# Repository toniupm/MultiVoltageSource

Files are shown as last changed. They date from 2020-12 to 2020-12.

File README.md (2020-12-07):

# MultiVoltageSource

<b> Design and Programming by Antonio Perez-Serrano </b> 

<b> PCB Design by Jose David Ayala </b> 

<i> CEMDATIC - ETSI Telecomunicación, Universidad Politécnica de Madrid (UPM) </i>

Version 1.0 - December 2020

<p align="center">
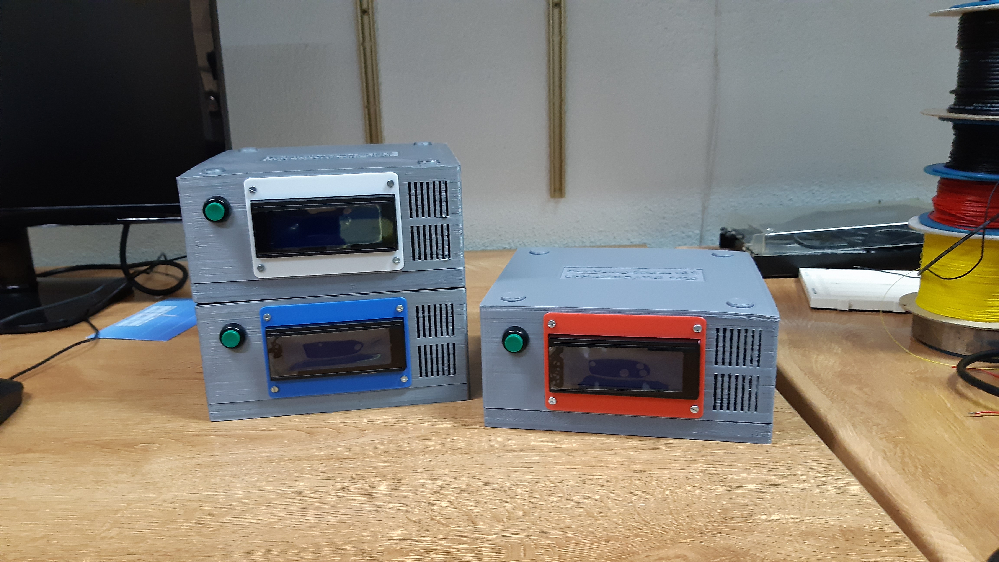
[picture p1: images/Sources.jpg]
MultiVoltageSources finished and ready to work.

</p>

<p align="justify"> Here we describe the MultiVoltageSource project, a voltage source with 7 channels used to power up photonic integrated circuits. </p>

<p align="justify">
     The <b> hardware </b> is based on negative linear regulators <a href="https://www.analog.com/en/products/lt3090.html#product-overview" target="_blank">LT3090</a> and digital potentiometers <a href="https://www.analog.com/en/products/ad5290.html" target="_blank">AD5290</a> controlled by an Arduino Nano <a href="https://store.arduino.cc/arduino-nano-every" target="_blank">Every</a> or <a href="https://store.arduino.cc/arduino-nano-33-iot" target="_blank">33 IOT</a>. It offers 7 channels ranging from -0.2 V to -10.2 V. A power supply of &plusmn; 15 V or &plusmn; 12 V is needed. The current output of the power supply must be choosen depending on the application, in our case a current output of 0.5 A is enough. The schematics and PCB design have been created using <a href="https://kicad.org/" target="_blank">KiCad</a> and they can be found in the <i> Kicad Project </i> folder. The MultiVoltageSource box has been designed using <a href="https://www.blender.org/" target="_blank">Blender</a>, it can be found in the <i> Blender Project </i> folder. The box can be 3D printed using PLA or ABS material and it is designed to use M3 bolts and nuts. The MultiVoltageSource is controlled via serial port, this allows to program voltage sweeps easily.   
</p>

<p align="center">
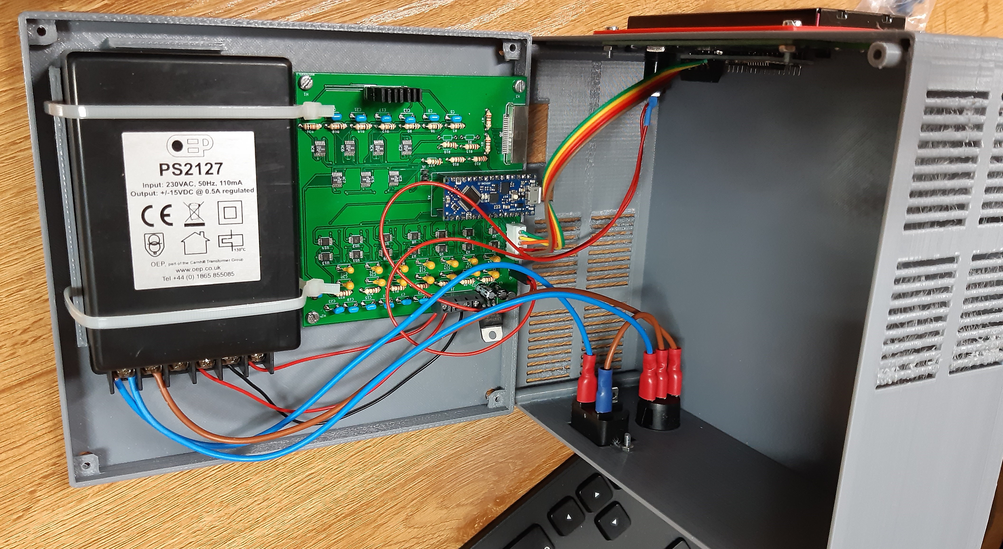
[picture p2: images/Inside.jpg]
Inside a MultiVoltageSource.

</p>

<p align="justify">
     The list of the materials used are:
     <ul>
          <li> 1 Arduino Nano <a href="https://store.arduino.cc/arduino-nano-every" target="_blank">Every</a> or <a href="https://store.arduino.cc/arduino-nano-33-iot" target="_blank">33 IOT</a> </li>
          <li> 7 chips <a href="https://www.analog.com/en/products/lt3090.html#product-overview" target="_blank">LT3090</a> </li>
          <li> 14 chips <a href="https://www.analog.com/en/products/ad5290.html" target="_blank">AD5290</a> </li>
          <li> 1 LCD display 20x4 characters </li>
          <li> 1 i2c/SPI LCD backpack <a href="https://learn.adafruit.com/i2c-spi-lcd-backpack" target="_blank">i2c/SPI LCD backpack</a> with the SPI enabled </li>
          <li> 1 Embedded Linear Power Supply Encapsulated PS2127 &plusmn; 15 V</li>
          <li> 1 Voltage Regulator to 5 V LD1085V50 </li>
          <li> 7 Resistors 2k &#8486; </li>
          <li> 7 Resistors 2.2k &#8486; </li>
          <li> 7 Resistors 10k &#8486; </li>
          <li> 7 Capacitors 4.7 uF </li>
          <li> 2 Capacitors 10 uF </li>
          <li> 14 Capacitors 100 nF </li>
          <li> Several PCB connectors including 1 <a href="https://www.samtec.com/products/fcs8-20-01-l-s-a-tr" target="_blank">FCS8-20-01-L-S-A-TR</a> connector </li>
          <li> 1 Switch </li>
          <li> 1 Button </li>
          <li> 1 Power Supply cable and connector </li>
          <li> Several cables </li>
     </ul>          
</p>

The cost of a MultiVoltage source is around 200 €.

<p align="center">
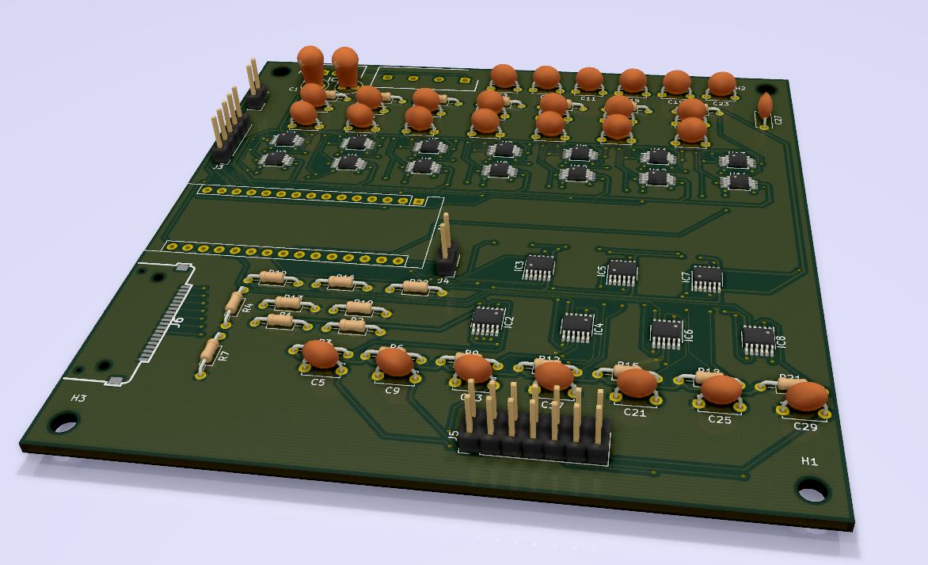
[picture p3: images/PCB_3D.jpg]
KiCad rendering of the PCB.

</p>

<p align="justify">
     The <b> software </b> can be found in the <i> Software </i> folder. It contains the Arduino Firmware and the LabVIEW project and functions to control the MultiVoltageSource. LabVIEW 2020 version has been used to create the controlling software. At this moment, only serial communication through a USB cable is supported. Next versions will include WiFi communication.   
</p>

<p align="center">
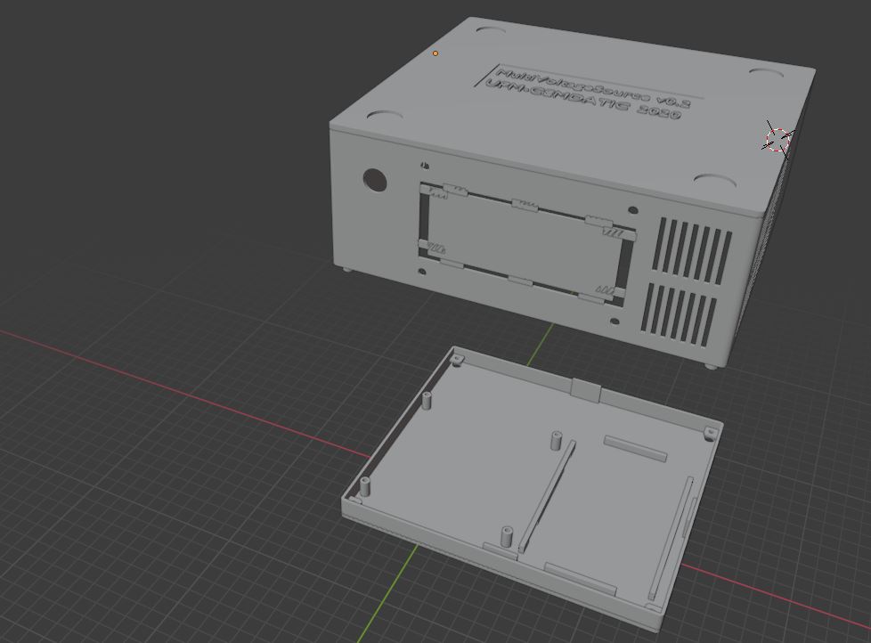
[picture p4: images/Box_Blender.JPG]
Blender snapshot of the box.

</p>

<p align="justify">
     Future improvements/changes:
          <ul>
               <li> WiFi communication using Arduino Nano 33 IOT </li>
               <li> Creation a stand-alone control software based on Processing </li>
          </ul>     
</p>

<p align="center">
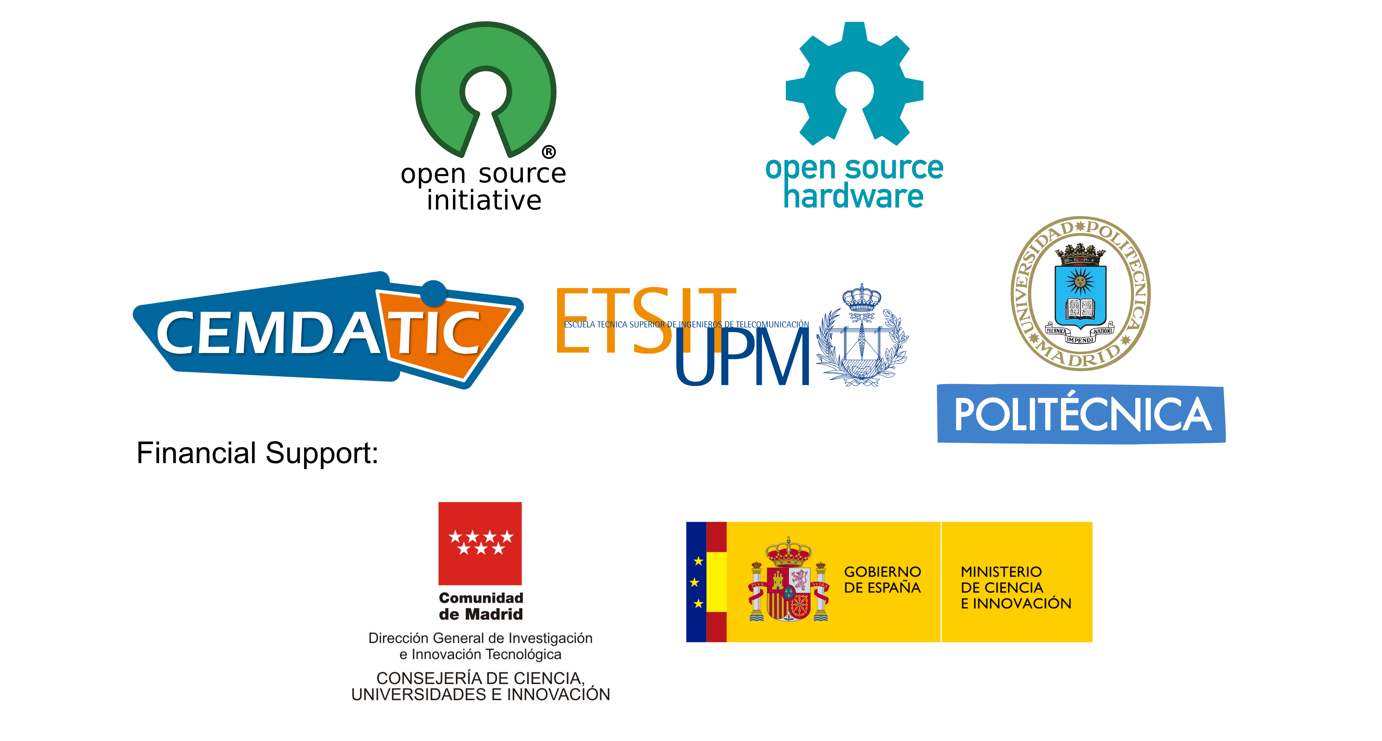
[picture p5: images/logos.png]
Logos

</p>

<p align="justify">
We acknowledge support from Comunidad de Madrid through project MULTI-GAS-PIC (APOYO-JOVENES-KXHJ8C-16-VCKM78) and Ministerio de Ciencia e Innovación of Spain through project LIDERA (RTI2018-094118-B-C21).
</p>

<p align="justify">
"Acción financiada por la Comunidad de Madrid en el marco del Convenio Plurianual con la Universidad Politécnica de Madrid <b> en la línea de actuación estímulo a la investigación de jóvenes doctores </b>"
</p>

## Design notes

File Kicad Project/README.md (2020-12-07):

This folder contains the KiCad project of the MultiVoltageSource, including schematics, PCB and final Gerber files.

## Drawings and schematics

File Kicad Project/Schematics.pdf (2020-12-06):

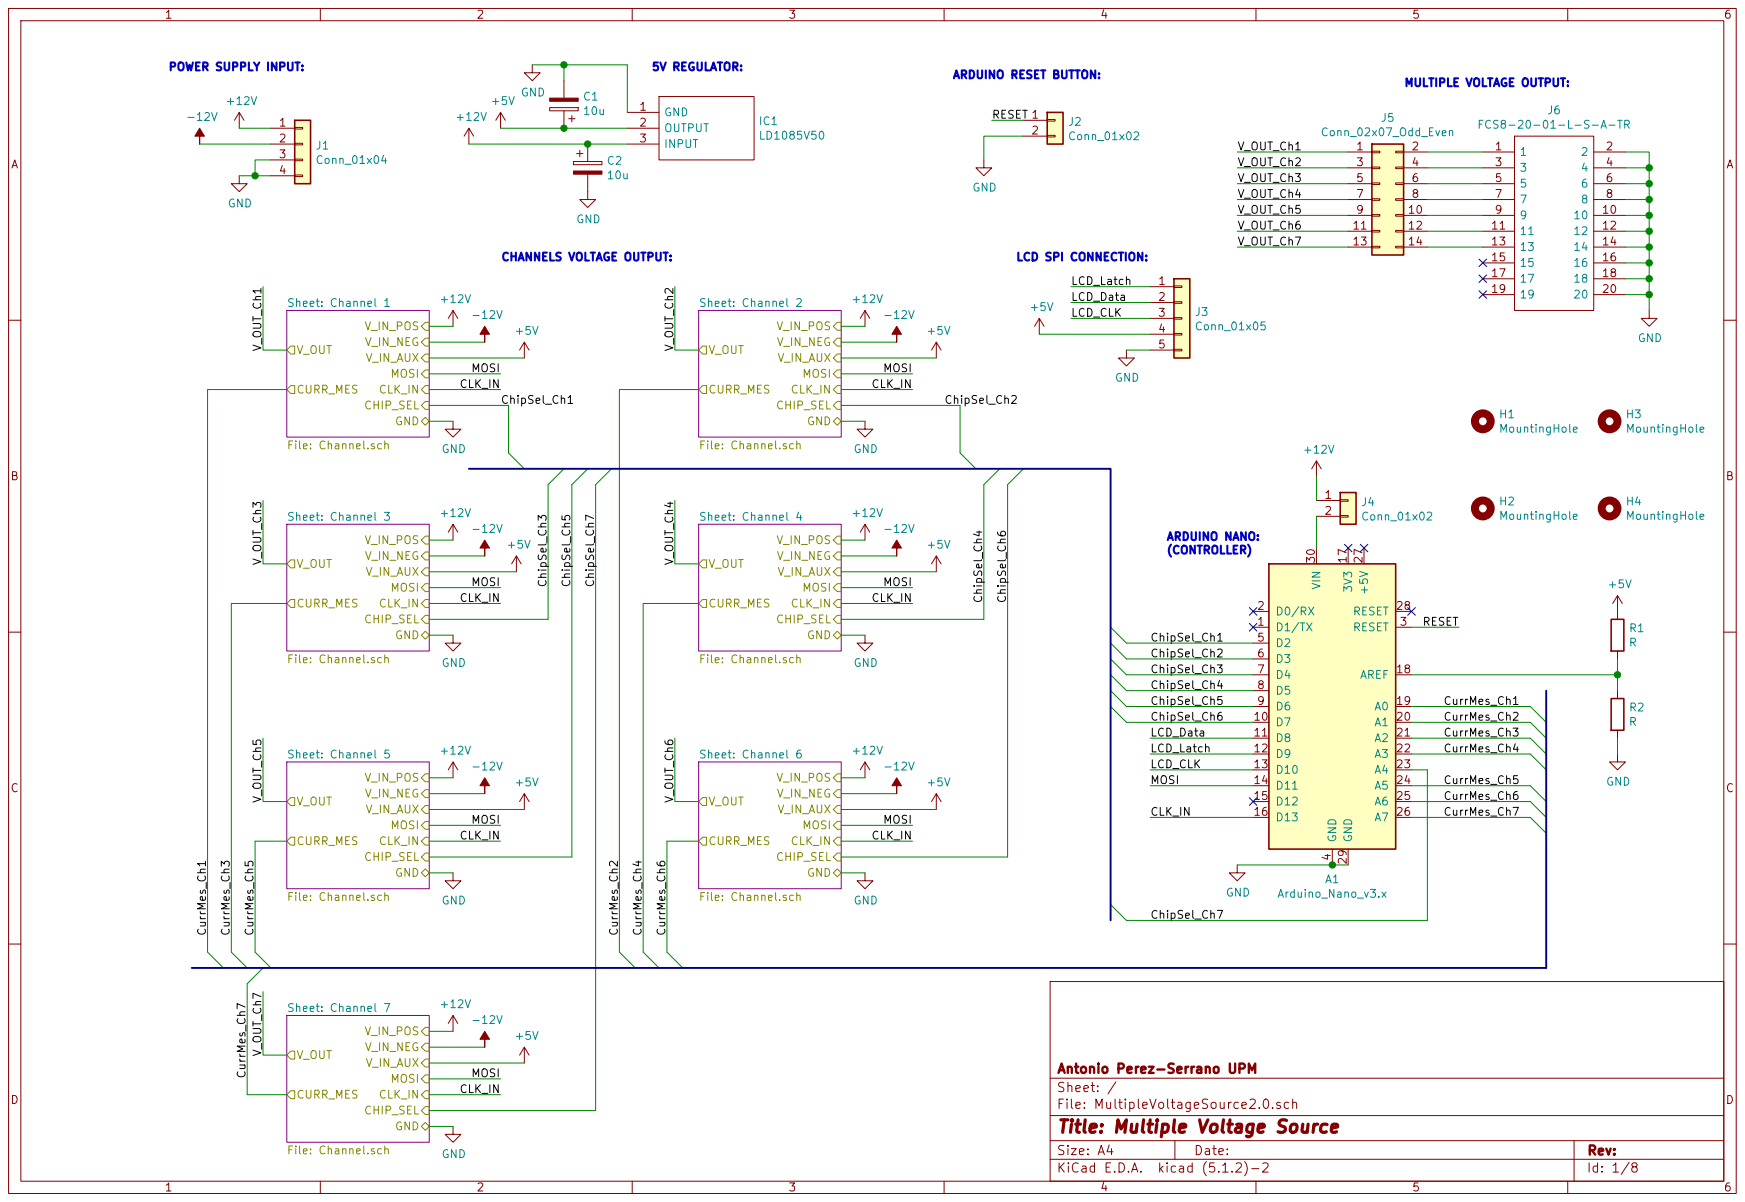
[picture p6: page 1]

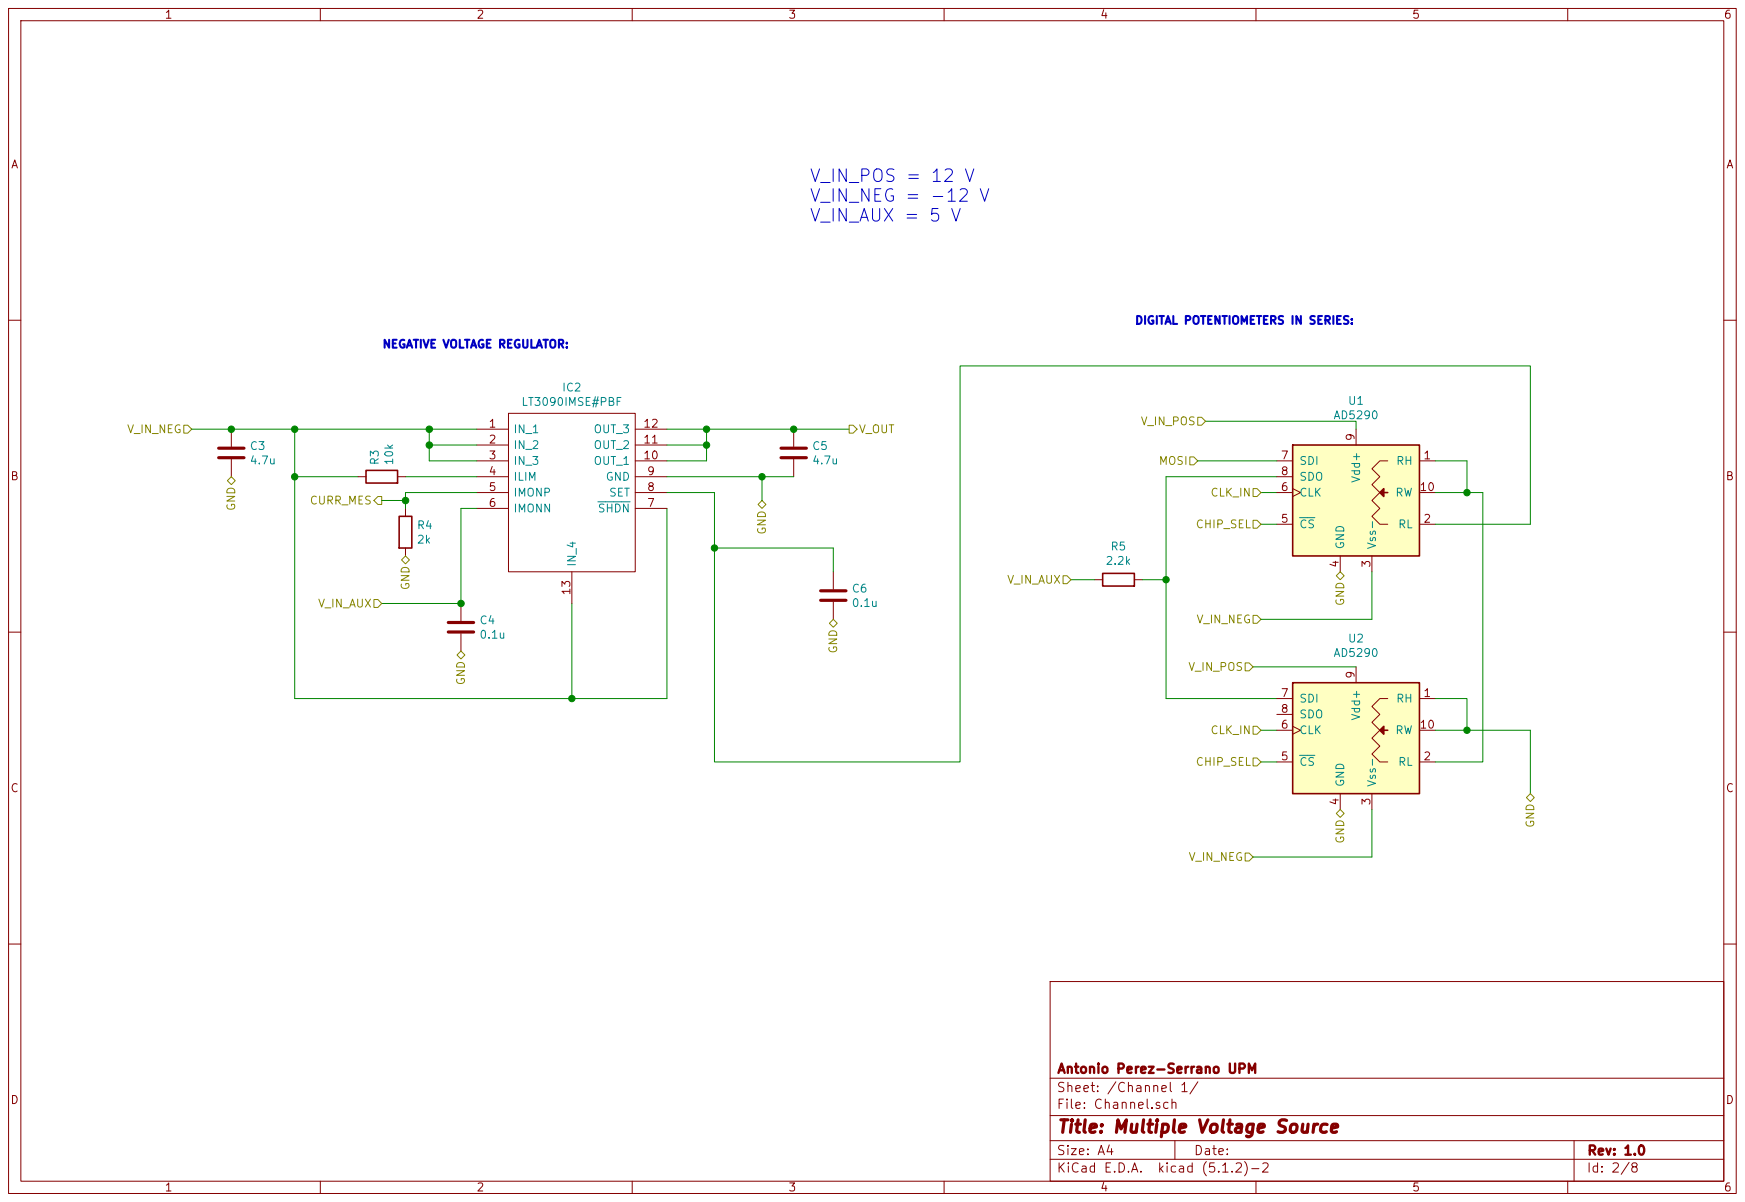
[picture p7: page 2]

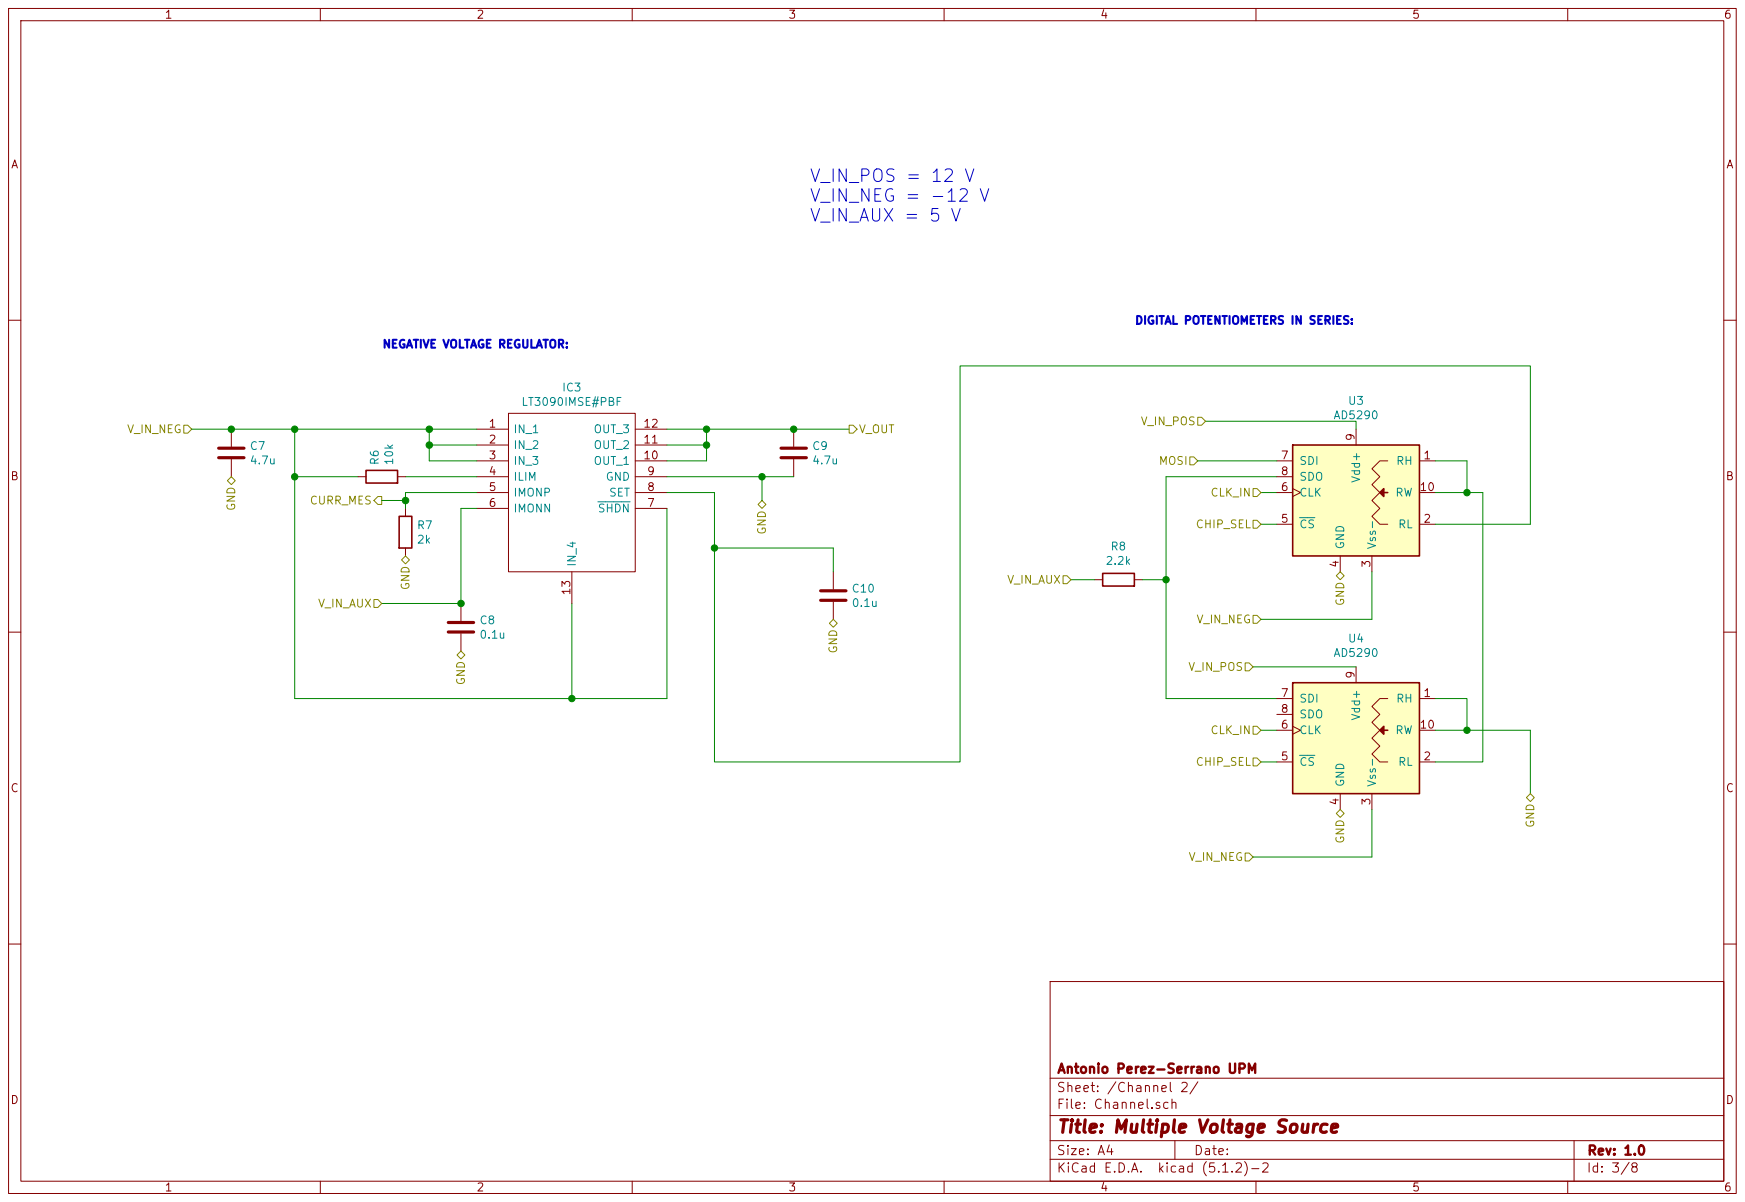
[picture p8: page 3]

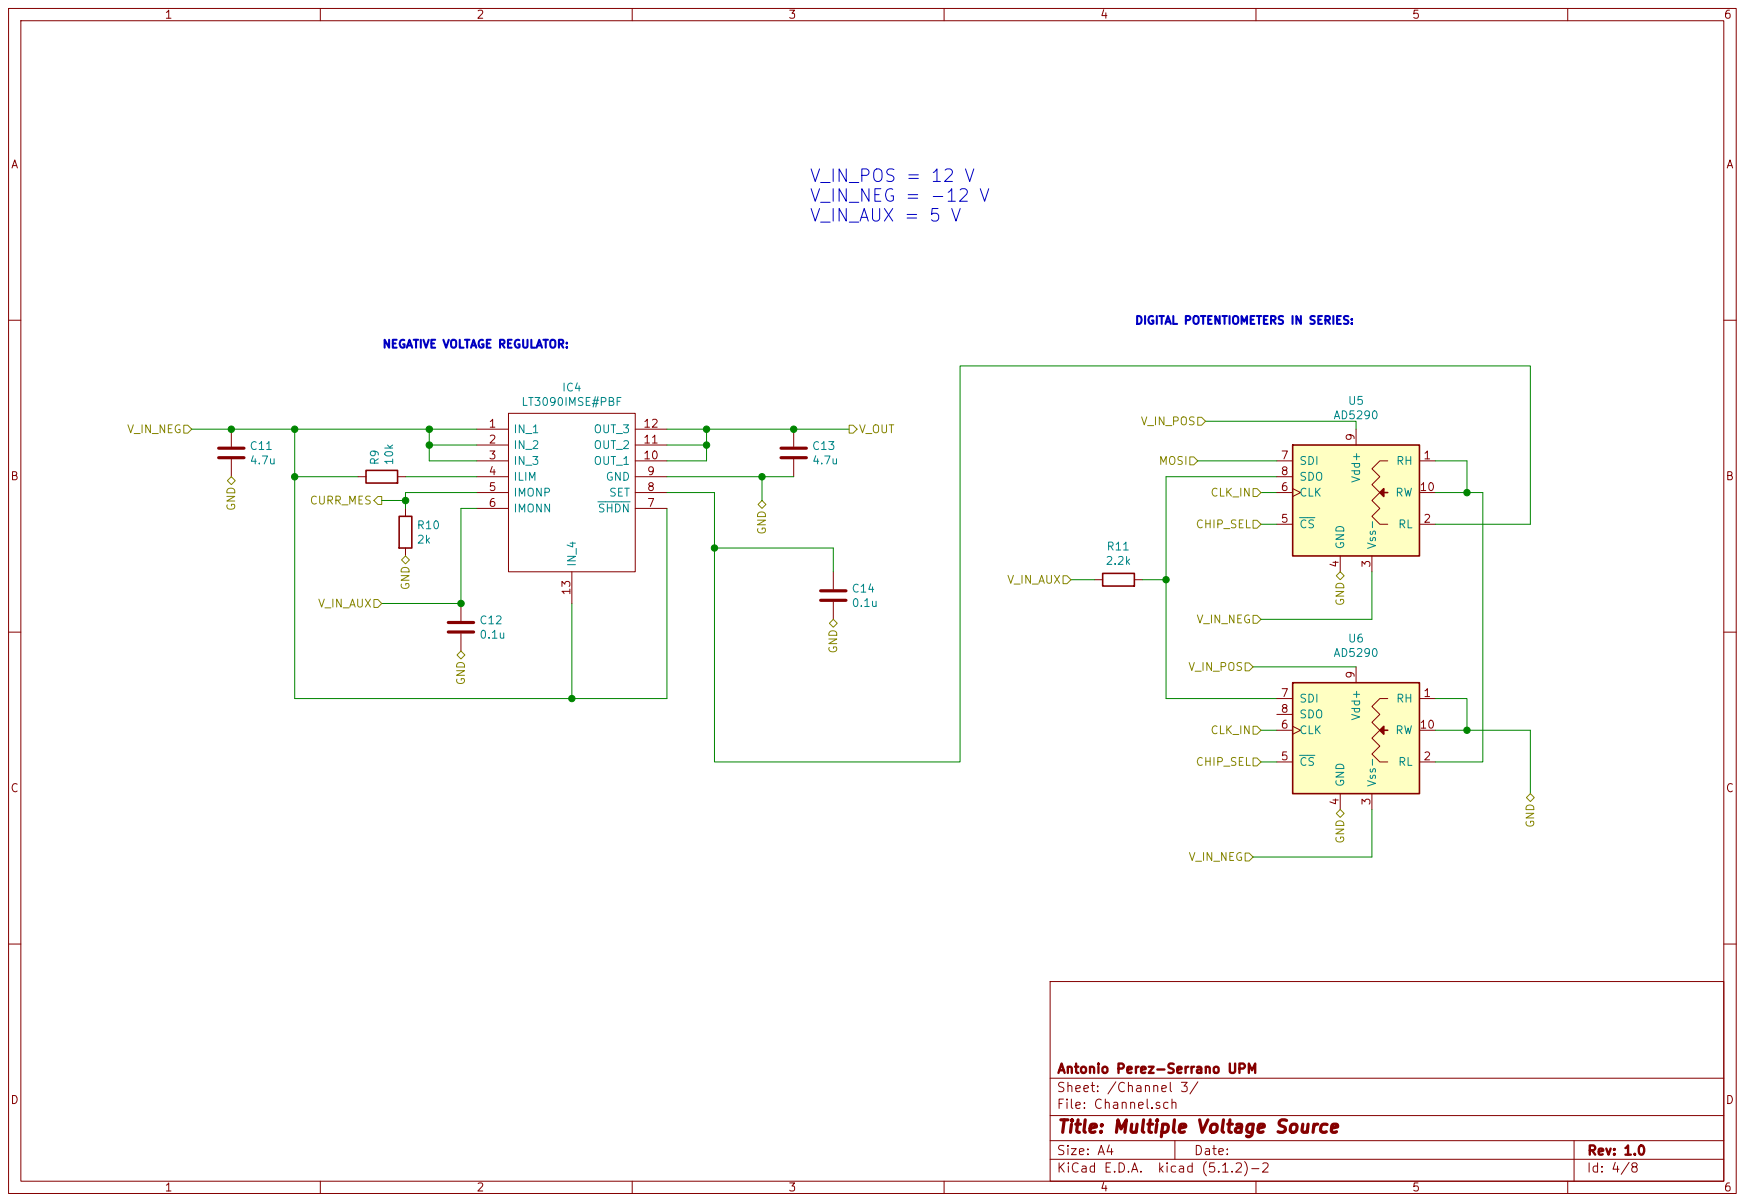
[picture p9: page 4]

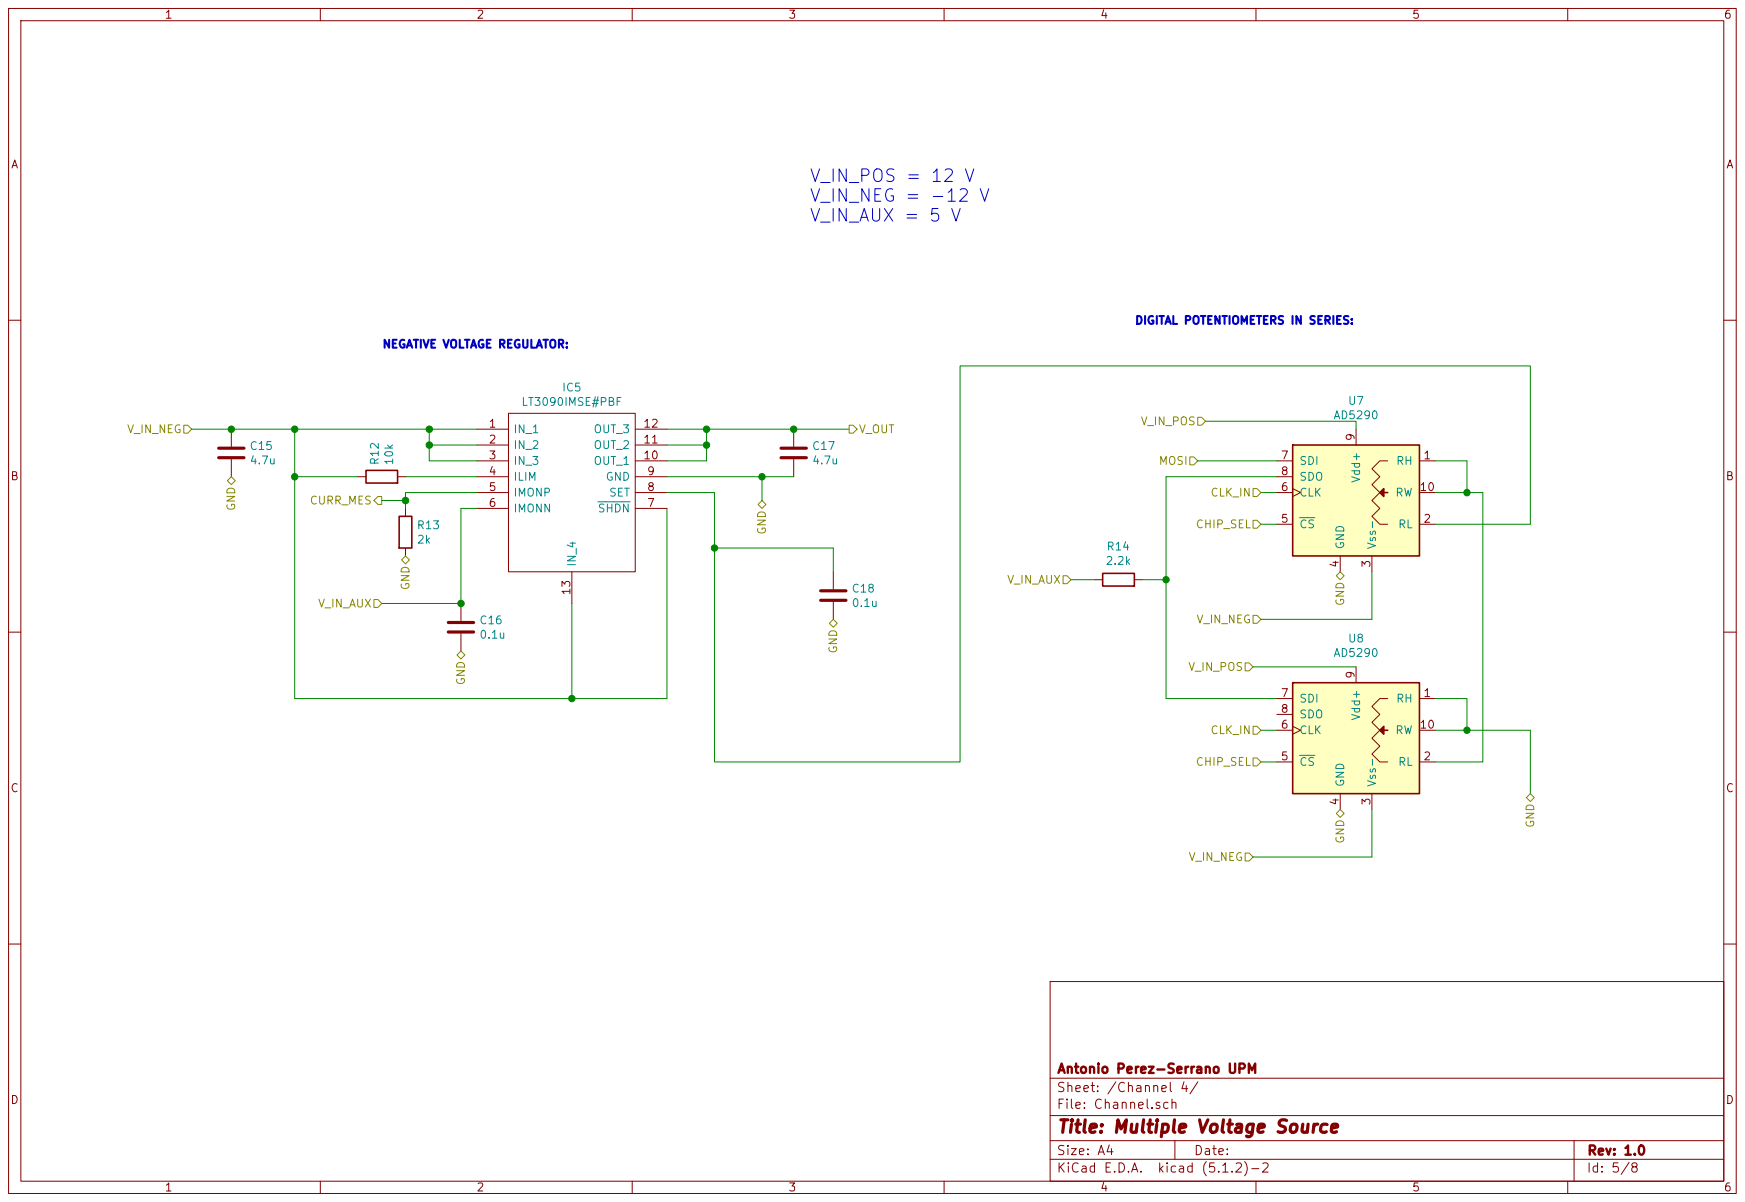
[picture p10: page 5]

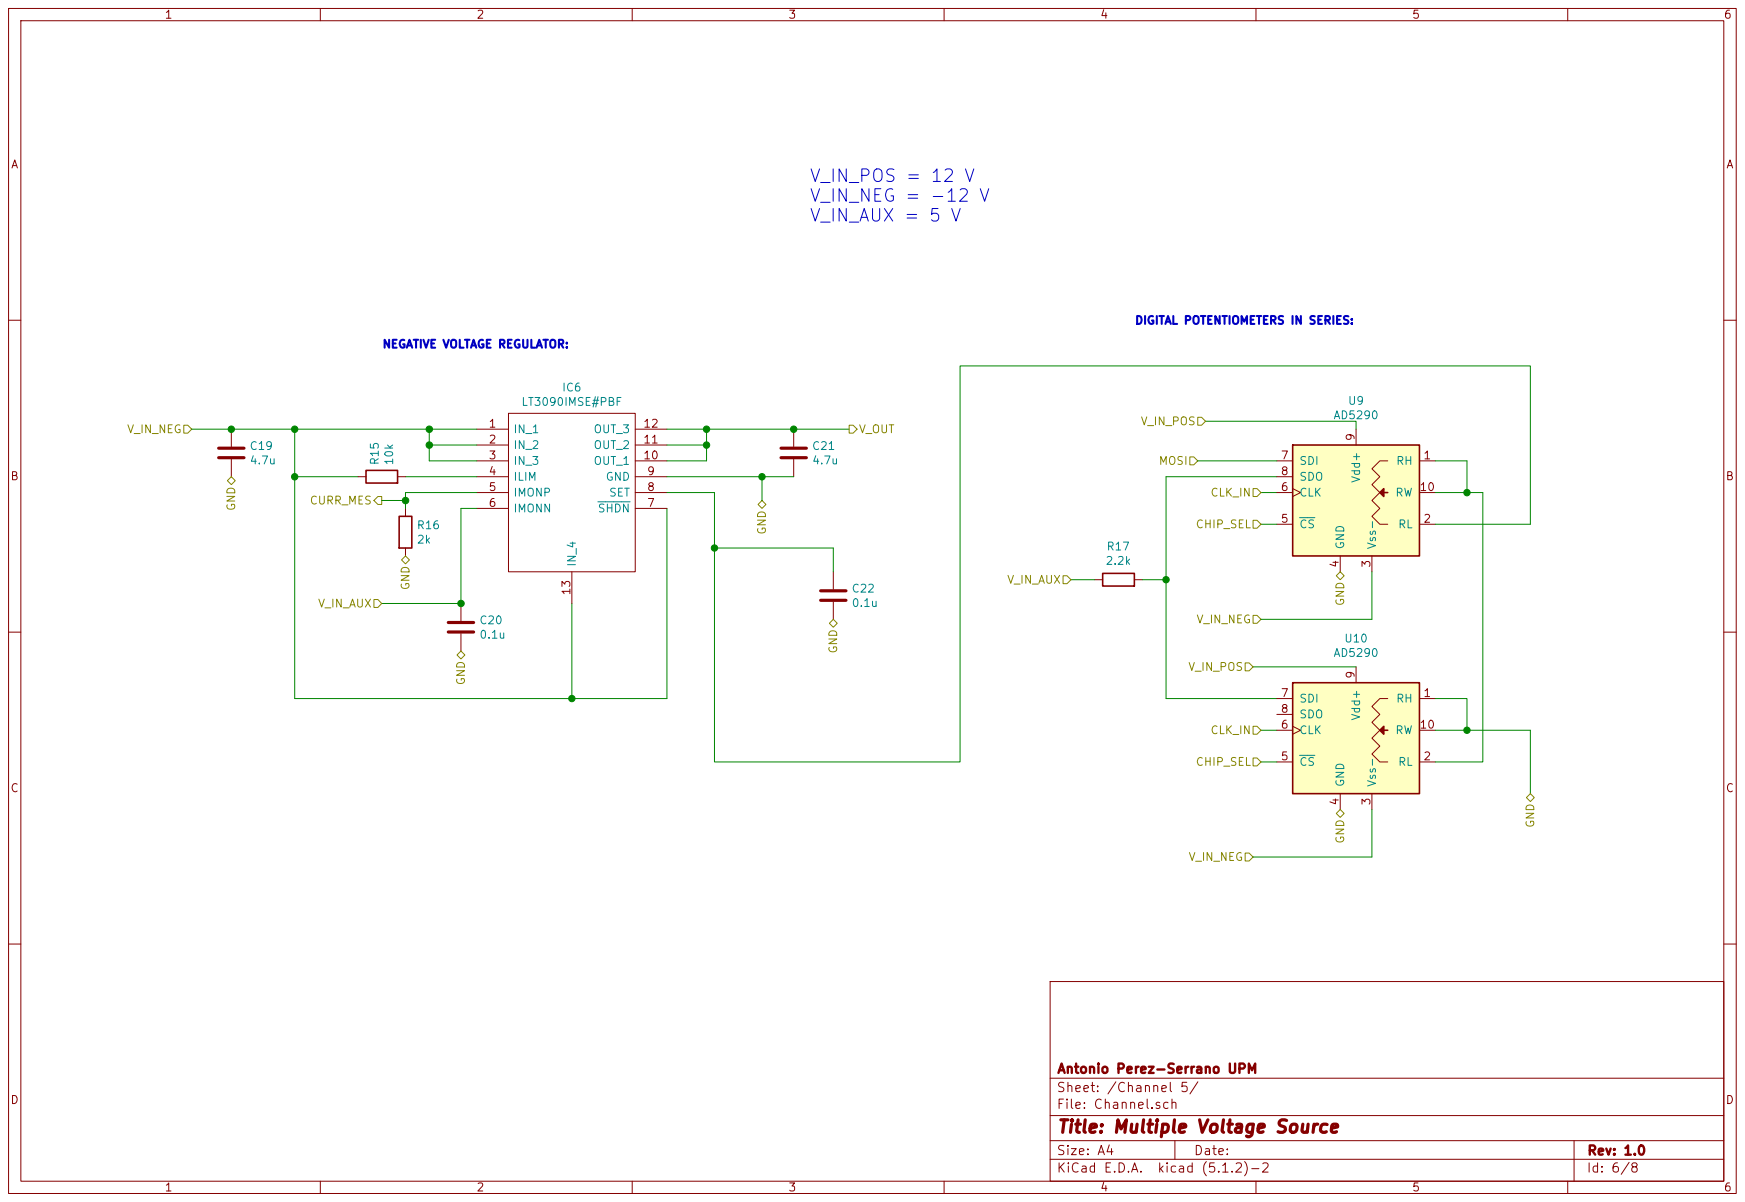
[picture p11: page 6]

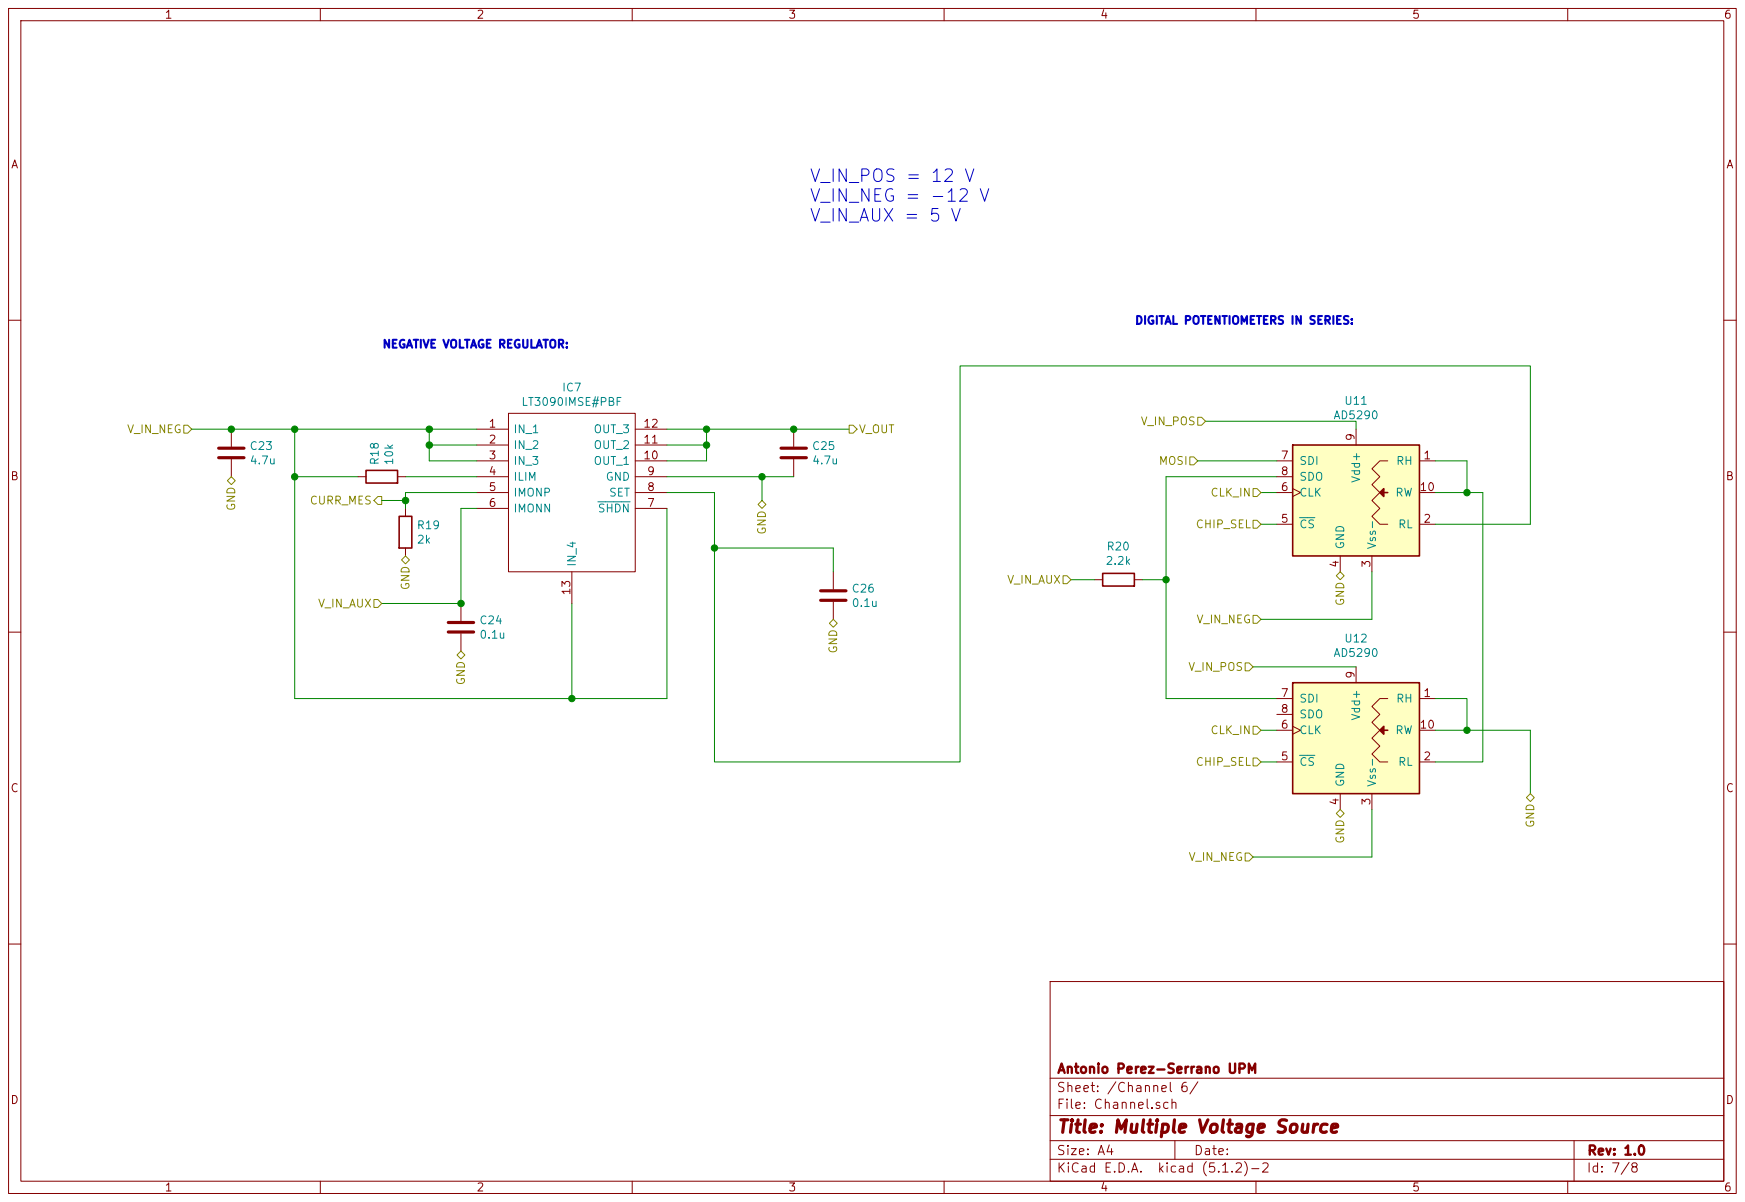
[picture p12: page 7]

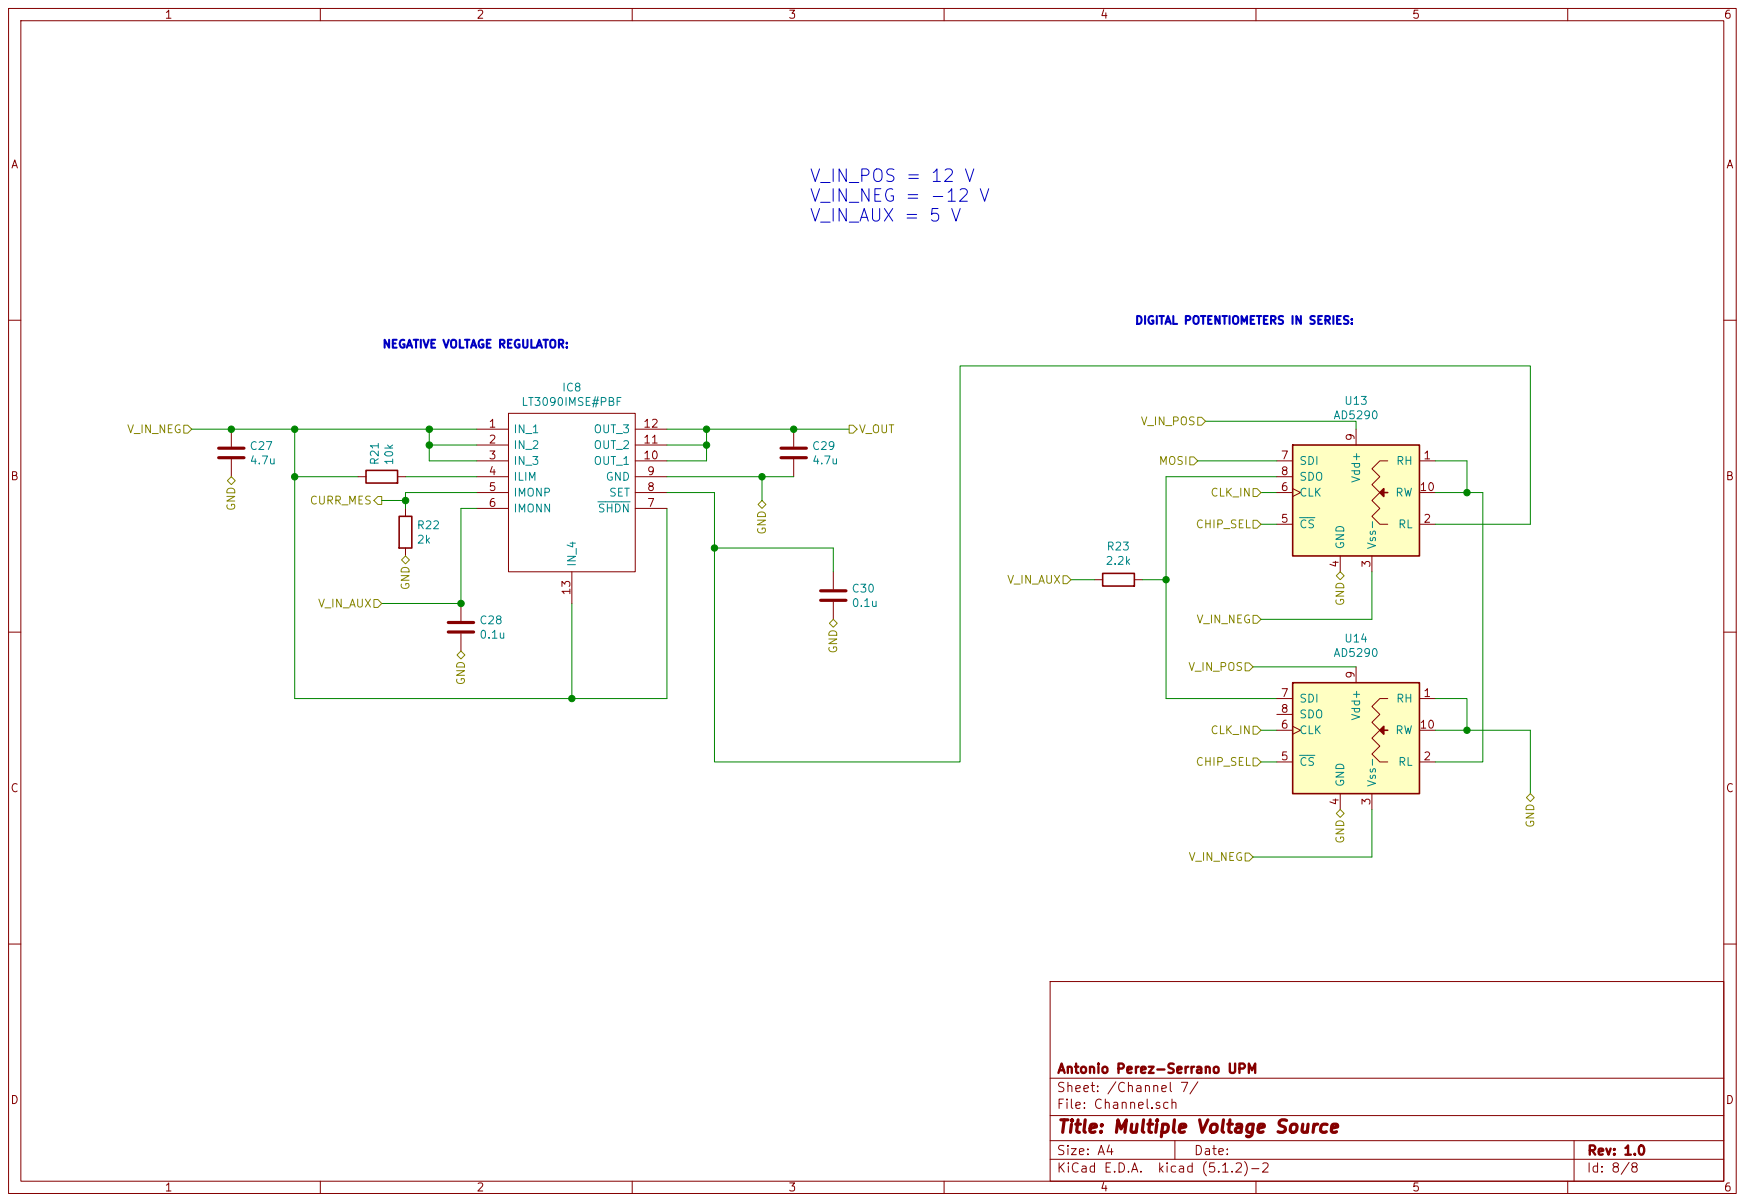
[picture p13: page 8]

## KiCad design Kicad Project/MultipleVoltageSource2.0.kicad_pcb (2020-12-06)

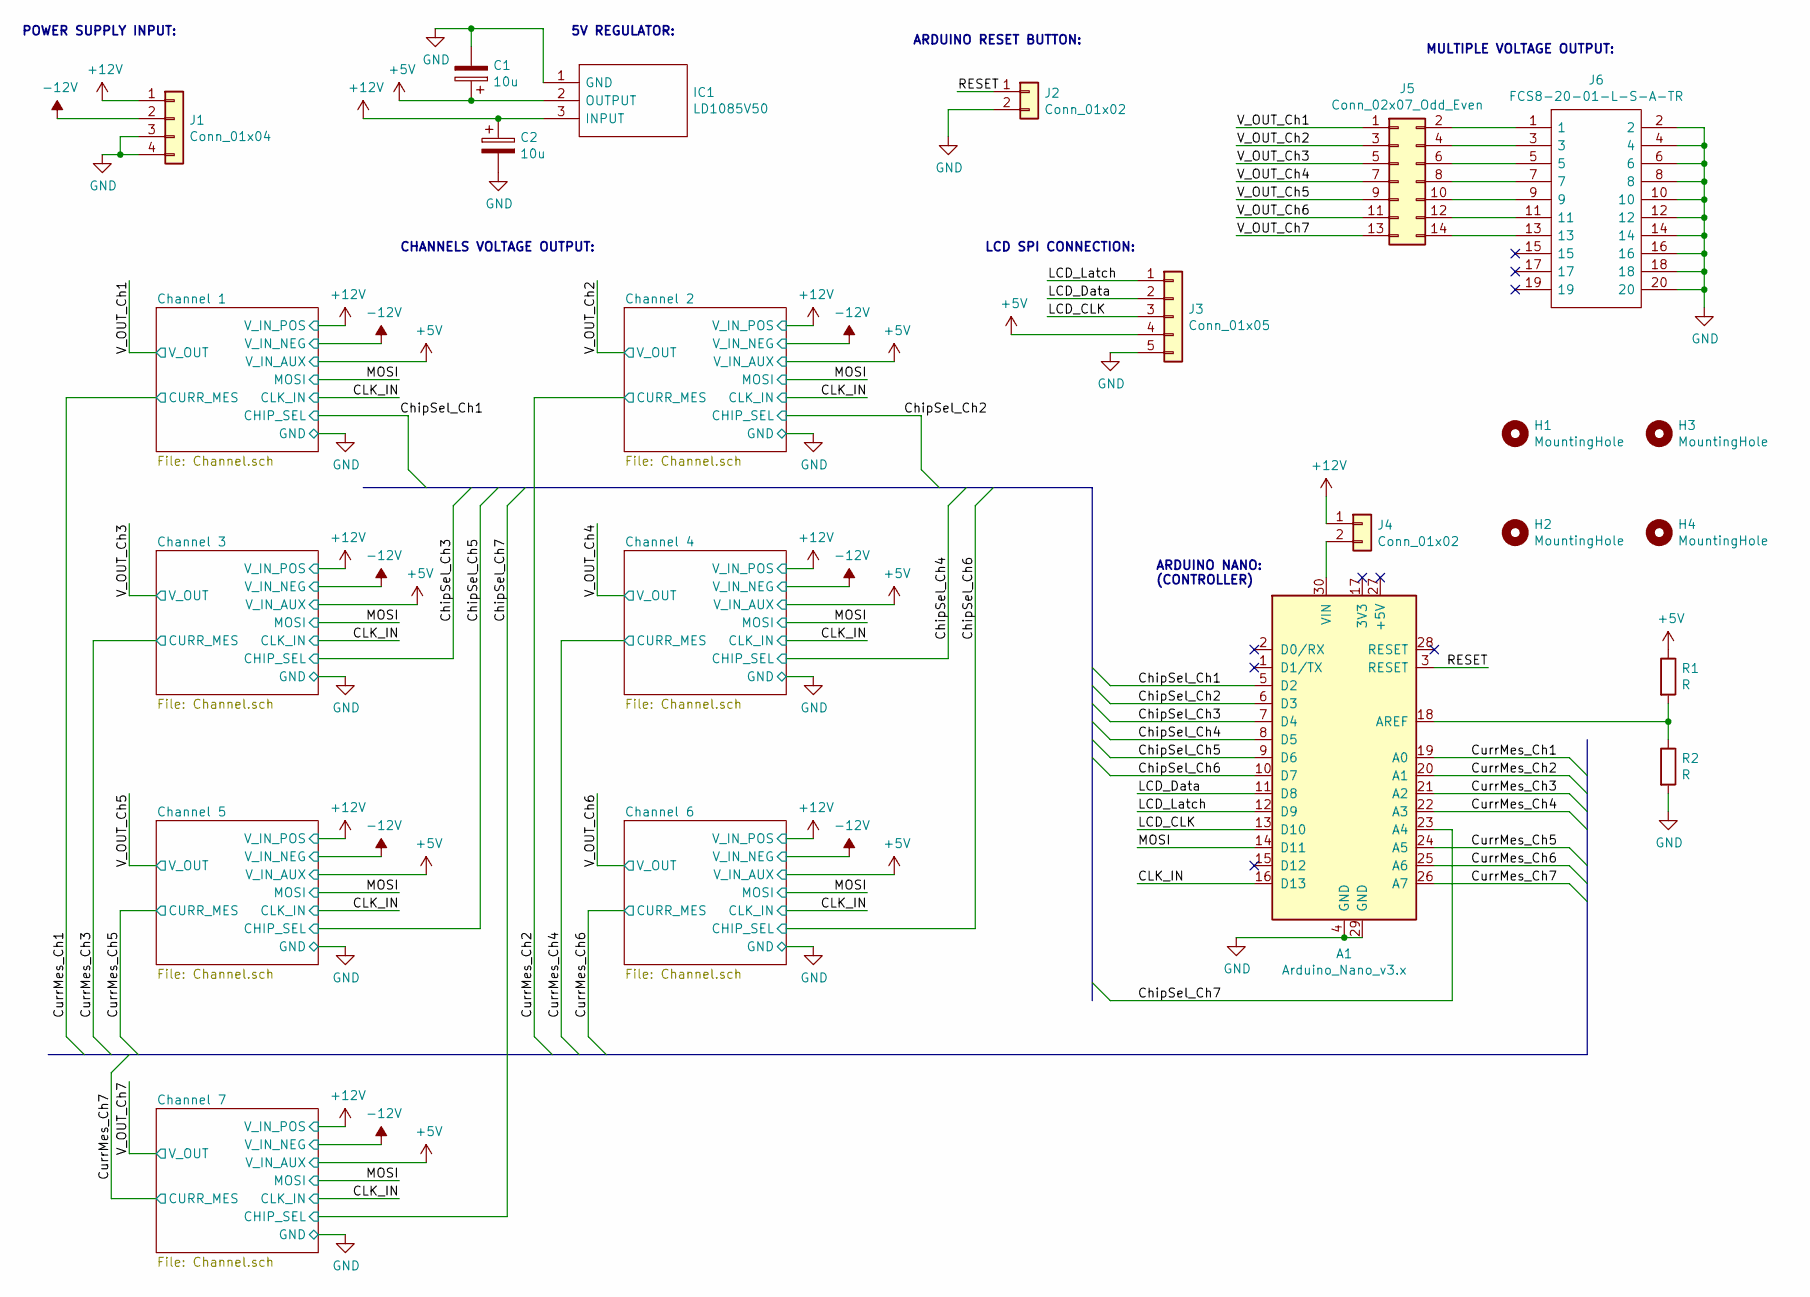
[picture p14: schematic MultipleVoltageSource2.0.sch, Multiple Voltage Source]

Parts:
A1: Arduino_Nano_v3.x; Arduino_Nano
C1, C2: 10u; CP_Radial_Tantal_D5.0mm_P2.50mm
H1, H2, H3, H4: MountingHole; MountingHole_3.2mm_M3
IC1: LD1085V50; TO270P460X1020X2008-3P; Mouser Part Number 511-LD1085V50
J1: Conn_01x04; SHDR4W100P0X500_1X4_2000X800X1000P
J2, J4: Conn_01x02; PinHeader_1x02_P2.54mm_Vertical
J3: Conn_01x05; PinHeader_1x05_P2.54mm_Vertical
J5: Conn_02x07_Odd_Even; PinHeader_2x07_P2.54mm_Vertical
J6: FCS8-20-01-L-S-A-TR; FCS8-20-01-X-S-A; Mouser Part Number 200-FCS82001LSATR
R1, R2: R; R_Axial_DIN0204_L3.6mm_D1.6mm_P7.62mm_Horizontal

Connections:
+5V: C1.1, IC1.2 (OUTPUT), J3.4, R1.1; also elsewhere on the board
+12V: C2.1, IC1.3 (INPUT), J1.1, J4.1; also elsewhere on the board
-12V: J1.2; also elsewhere on the board
/CLK_IN: A1.16 (D13); also elsewhere on the board
/ChipSel_Ch1: A1.5 (D2); also elsewhere on the board
/ChipSel_Ch2: A1.6 (D3); also elsewhere on the board
/ChipSel_Ch3: A1.7 (D4); also elsewhere on the board
/ChipSel_Ch4: A1.8 (D5); also elsewhere on the board
/ChipSel_Ch5: A1.9 (D6); also elsewhere on the board
/ChipSel_Ch6: A1.10 (D7); also elsewhere on the board
/ChipSel_Ch7: A1.23 (A4); also elsewhere on the board
/CurrMes_Ch1: A1.19 (A0); also elsewhere on the board
/CurrMes_Ch2: A1.20 (A1); also elsewhere on the board
/CurrMes_Ch3: A1.21 (A2); also elsewhere on the board
/CurrMes_Ch4: A1.22 (A3); also elsewhere on the board
/CurrMes_Ch5: A1.24 (A5); also elsewhere on the board
/CurrMes_Ch6: A1.25 (A6); also elsewhere on the board
/CurrMes_Ch7: A1.26 (A7); also elsewhere on the board
/LCD_CLK: A1.13 (D10), J3.3
/LCD_Data: A1.11 (D8), J3.2
/LCD_Latch: A1.12 (D9), J3.1
/MOSI: A1.14 (D11); also elsewhere on the board
/RESET: A1.3 (RESET), J2.1
/V_OUT_Ch1: J5.1; also elsewhere on the board
/V_OUT_Ch2: J5.3; also elsewhere on the board
/V_OUT_Ch3: J5.5; also elsewhere on the board
/V_OUT_Ch4: J5.7; also elsewhere on the board
/V_OUT_Ch5: J5.9; also elsewhere on the board
/V_OUT_Ch6: J5.11; also elsewhere on the board
/V_OUT_Ch7: J5.13; also elsewhere on the board
GND: A1.4 (GND), A1.29 (GND), C1.2, C2.2, IC1.1 (GND), J1.3, J1.4, J2.2, J3.5, J6.2, J6.4, J6.6, J6.8, J6.10, J6.12, J6.14, J6.16, J6.18, J6.20, R2.2; also elsewhere on the board
unnamed: A1.18 (AREF), R1.2, R2.1
unnamed: A1.30 (VIN), J4.2
unnamed: J5.2, J6.1
unnamed: J5.4, J6.3
unnamed: J5.6, J6.5
unnamed: J5.8, J6.7
unnamed: J5.10, J6.9
unnamed: J5.12, J6.11
unnamed: J5.14, J6.13

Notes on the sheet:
POWER SUPPLY INPUT:
LCD SPI CONNECTION:
MULTIPLE VOLTAGE OUTPUT:
ARDUINO NANO: (CONTROLLER)
CHANNELS VOLTAGE OUTPUT:
5V REGULATOR:
ARDUINO RESET BUTTON:

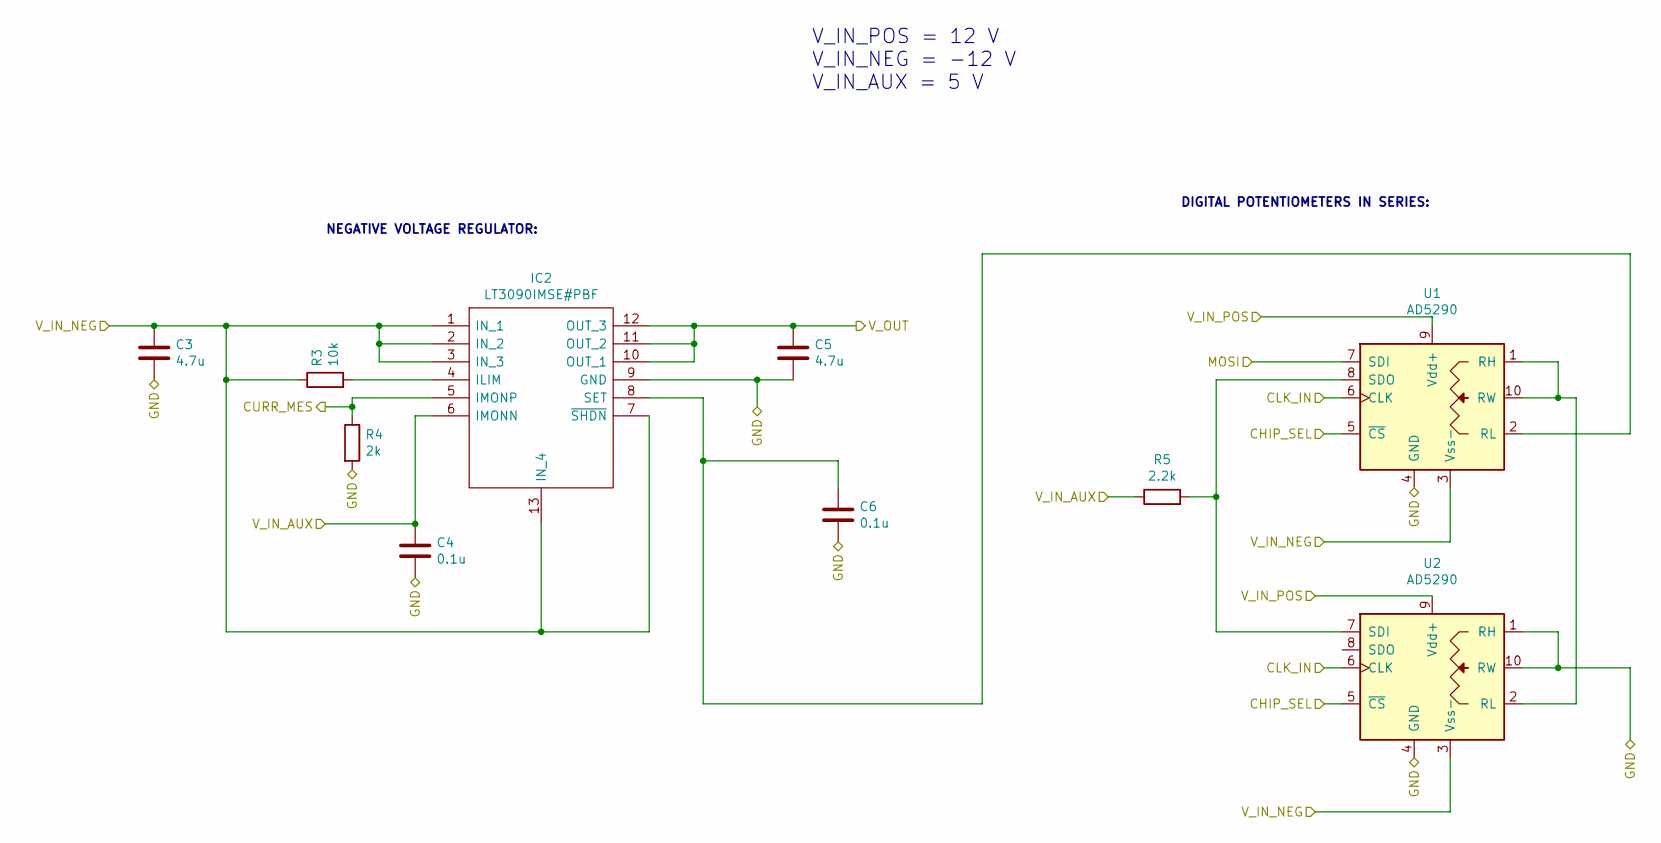
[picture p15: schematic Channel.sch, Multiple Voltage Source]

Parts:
C3, C5: 4.7u; C_Disc_D5.0mm_W2.5mm_P5.00mm
C4, C6: 0.1u; C_Disc_D5.0mm_W2.5mm_P5.00mm
IC2: LT3090IMSE#PBF; MSOP-12-1EP_3x4mm_P0.65mm_EP1.65x2.85mm; Manufacturer_Part_Number LT3090IMSE#PBF
R3: 10k; R_Axial_DIN0204_L3.6mm_D1.6mm_P7.62mm_Horizontal
R4: 2k; R_Axial_DIN0204_L3.6mm_D1.6mm_P7.62mm_Horizontal
R5: 2.2k; R_Axial_DIN0204_L3.6mm_D1.6mm_P7.62mm_Horizontal
U1, U2: AD5290; MSOP-10_3x3mm_P0.5mm

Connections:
+5V: C4.1, IC2.6 (IMONN), R5.1; also elsewhere on the board
+12V: U1.9 (Vdd+), U2.9 (Vdd+); also elsewhere on the board
-12V: C3.1, IC2.1 (IN_1), IC2.2 (IN_2), IC2.3 (IN_3), IC2.7 (~SHDN), IC2.13 (IN_4), R3.1, U1.3 (Vss-), U2.3 (Vss-); also elsewhere on the board
/CLK_IN: U1.6 (CLK), U2.6 (CLK); also elsewhere on the board
/ChipSel_Ch1: U1.5 (~CS~), U2.5 (~CS~); also elsewhere on the board
/CurrMes_Ch1: IC2.5 (IMONP), R4.1; also elsewhere on the board
/MOSI: U1.7 (SDI); also elsewhere on the board
/V_OUT_Ch1: C5.1, IC2.10 (OUT_1), IC2.11 (OUT_2), IC2.12 (OUT_3); also elsewhere on the board
GND: C3.2, C4.2, C5.2, C6.2, IC2.9 (GND), R4.2, U1.4 (GND), U2.1 (RH), U2.4 (GND), U2.10 (RW); also elsewhere on the board
unnamed: C6.1, IC2.8 (SET), U1.2 (RL)
unnamed: IC2.4 (ILIM), R3.2
unnamed: R5.2, U1.8 (SDO), U2.7 (SDI)
unnamed: U1.1 (RH), U1.10 (RW), U2.2 (RL)

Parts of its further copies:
C7, C9, C11, C13, C15, C17, C19, C21, C23, C25, C27, C29: 4.7u; C_Disc_D5.0mm_W2.5mm_P5.00mm
C8, C10, C12, C14, C16, C18, C20, C22, C24, C26, C28, C30: 0.1u; C_Disc_D5.0mm_W2.5mm_P5.00mm
IC3, IC4, IC5, IC6, IC7, IC8: LT3090IMSE#PBF; MSOP-12-1EP_3x4mm_P0.65mm_EP1.65x2.85mm; Manufacturer_Part_Number LT3090IMSE#PBF
R6, R9, R12, R15, R18, R21: 10k; R_Axial_DIN0204_L3.6mm_D1.6mm_P7.62mm_Horizontal
R7, R10, R13, R16, R19, R22: 2k; R_Axial_DIN0204_L3.6mm_D1.6mm_P7.62mm_Horizontal
R8, R11, R14, R17, R20, R23: 2.2k; R_Axial_DIN0204_L3.6mm_D1.6mm_P7.62mm_Horizontal
U3, U4, U5, U6, U7, U8, U9, U10, U11, U12, U13, U14: AD5290; MSOP-10_3x3mm_P0.5mm

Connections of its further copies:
+5V: C8.1, C12.1, C16.1, C20.1, C24.1, C28.1, IC3.6 (IMONN), IC4.6 (IMONN), IC5.6 (IMONN), IC6.6 (IMONN), IC7.6 (IMONN), IC8.6 (IMONN), R8.1, R11.1, R14.1, R17.1, R20.1, R23.1; also elsewhere on the board
+12V: U3.9 (Vdd+), U4.9 (Vdd+), U5.9 (Vdd+), U6.9 (Vdd+), U7.9 (Vdd+), U8.9 (Vdd+), U9.9 (Vdd+), U10.9 (Vdd+), U11.9 (Vdd+), U12.9 (Vdd+), U13.9 (Vdd+), U14.9 (Vdd+); also elsewhere on the board
-12V: C7.1, C11.1, C15.1, C19.1, C23.1, C27.1, IC3.1 (IN_1), IC3.2 (IN_2), IC3.3 (IN_3), IC3.7 (~SHDN), IC3.13 (IN_4), IC4.1 (IN_1), IC4.2 (IN_2), IC4.3 (IN_3), IC4.7 (~SHDN), IC4.13 (IN_4), IC5.1 (IN_1), IC5.2 (IN_2), IC5.3 (IN_3), IC5.7 (~SHDN), IC5.13 (IN_4), IC6.1 (IN_1), IC6.2 (IN_2), IC6.3 (IN_3), IC6.7 (~SHDN), IC6.13 (IN_4), IC7.1 (IN_1), IC7.2 (IN_2), IC7.3 (IN_3), IC7.7 (~SHDN), IC7.13 (IN_4), IC8.1 (IN_1), IC8.2 (IN_2), IC8.3 (IN_3), IC8.7 (~SHDN), IC8.13 (IN_4), R6.1, R9.1, R12.1, R15.1, R18.1, R21.1, U3.3 (Vss-), U4.3 (Vss-), U5.3 (Vss-), U6.3 (Vss-), U7.3 (Vss-), U8.3 (Vss-), U9.3 (Vss-), U10.3 (Vss-), U11.3 (Vss-), U12.3 (Vss-), U13.3 (Vss-), U14.3 (Vss-); also elsewhere on the board
/CLK_IN: U3.6 (CLK), U4.6 (CLK), U5.6 (CLK), U6.6 (CLK), U7.6 (CLK), U8.6 (CLK), U9.6 (CLK), U10.6 (CLK), U11.6 (CLK), U12.6 (CLK), U13.6 (CLK), U14.6 (CLK); also elsewhere on the board
/ChipSel_Ch2: U3.5 (~CS~), U4.5 (~CS~); also elsewhere on the board
/ChipSel_Ch3: U5.5 (~CS~), U6.5 (~CS~); also elsewhere on the board
/ChipSel_Ch4: U7.5 (~CS~), U8.5 (~CS~); also elsewhere on the board
/ChipSel_Ch5: U9.5 (~CS~), U10.5 (~CS~); also elsewhere on the board
/ChipSel_Ch6: U11.5 (~CS~), U12.5 (~CS~); also elsewhere on the board
/ChipSel_Ch7: U13.5 (~CS~), U14.5 (~CS~); also elsewhere on the board
/CurrMes_Ch2: IC3.5 (IMONP), R7.1; also elsewhere on the board
/CurrMes_Ch3: IC4.5 (IMONP), R10.1; also elsewhere on the board
/CurrMes_Ch4: IC5.5 (IMONP), R13.1; also elsewhere on the board
/CurrMes_Ch5: IC6.5 (IMONP), R16.1; also elsewhere on the board
/CurrMes_Ch6: IC7.5 (IMONP), R19.1; also elsewhere on the board
/CurrMes_Ch7: IC8.5 (IMONP), R22.1; also elsewhere on the board
/MOSI: U3.7 (SDI), U5.7 (SDI), U7.7 (SDI), U9.7 (SDI), U11.7 (SDI), U13.7 (SDI); also elsewhere on the board
/V_OUT_Ch2: C9.1, IC3.10 (OUT_1), IC3.11 (OUT_2), IC3.12 (OUT_3); also elsewhere on the board
/V_OUT_Ch3: C13.1, IC4.10 (OUT_1), IC4.11 (OUT_2), IC4.12 (OUT_3); also elsewhere on the board
/V_OUT_Ch4: C17.1, IC5.10 (OUT_1), IC5.11 (OUT_2), IC5.12 (OUT_3); also elsewhere on the board
/V_OUT_Ch5: C21.1, IC6.10 (OUT_1), IC6.11 (OUT_2), IC6.12 (OUT_3); also elsewhere on the board
/V_OUT_Ch6: C25.1, IC7.10 (OUT_1), IC7.11 (OUT_2), IC7.12 (OUT_3); also elsewhere on the board
/V_OUT_Ch7: C29.1, IC8.10 (OUT_1), IC8.11 (OUT_2), IC8.12 (OUT_3); also elsewhere on the board
GND: C7.2, C8.2, C9.2, C10.2, C11.2, C12.2, C13.2, C14.2, C15.2, C16.2, C17.2, C18.2, C19.2, C20.2, C21.2, C22.2, C23.2, C24.2, C25.2, C26.2, C27.2, C28.2, C29.2, C30.2, IC3.9 (GND), IC4.9 (GND), IC5.9 (GND), IC6.9 (GND), IC7.9 (GND), IC8.9 (GND), R7.2, R10.2, R13.2, R16.2, R19.2, R22.2, U3.4 (GND), U4.1 (RH), U4.4 (GND), U4.10 (RW), U5.4 (GND), U6.1 (RH), U6.4 (GND), U6.10 (RW), U7.4 (GND), U8.1 (RH), U8.4 (GND), U8.10 (RW), U9.4 (GND), U10.1 (RH), U10.4 (GND), U10.10 (RW), U11.4 (GND), U12.1 (RH), U12.4 (GND), U12.10 (RW), U13.4 (GND), U14.1 (RH), U14.4 (GND), U14.10 (RW); also elsewhere on the board
unnamed: C10.1, IC3.8 (SET), U3.2 (RL)
unnamed: C14.1, IC4.8 (SET), U5.2 (RL)
unnamed: C18.1, IC5.8 (SET), U7.2 (RL)
unnamed: C22.1, IC6.8 (SET), U9.2 (RL)
unnamed: C26.1, IC7.8 (SET), U11.2 (RL)
unnamed: C30.1, IC8.8 (SET), U13.2 (RL)
unnamed: IC3.4 (ILIM), R6.2
unnamed: IC4.4 (ILIM), R9.2
unnamed: IC5.4 (ILIM), R12.2
unnamed: IC6.4 (ILIM), R15.2
unnamed: IC7.4 (ILIM), R18.2
unnamed: IC8.4 (ILIM), R21.2
unnamed: R8.2, U3.8 (SDO), U4.7 (SDI)
unnamed: R11.2, U5.8 (SDO), U6.7 (SDI)
unnamed: R14.2, U7.8 (SDO), U8.7 (SDI)
unnamed: R17.2, U9.8 (SDO), U10.7 (SDI)
unnamed: R20.2, U11.8 (SDO), U12.7 (SDI)
unnamed: R23.2, U13.8 (SDO), U14.7 (SDI)
unnamed: U3.1 (RH), U3.10 (RW), U4.2 (RL)
unnamed: U5.1 (RH), U5.10 (RW), U6.2 (RL)
unnamed: U7.1 (RH), U7.10 (RW), U8.2 (RL)
unnamed: U9.1 (RH), U9.10 (RW), U10.2 (RL)
unnamed: U11.1 (RH), U11.10 (RW), U12.2 (RL)
unnamed: U13.1 (RH), U13.10 (RW), U14.2 (RL)

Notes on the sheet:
V_IN_POS = 12 V V_IN_NEG = -12 V V_IN_AUX = 5 V
NEGATIVE VOLTAGE REGULATOR:
DIGITAL POTENTIOMETERS IN SERIES:

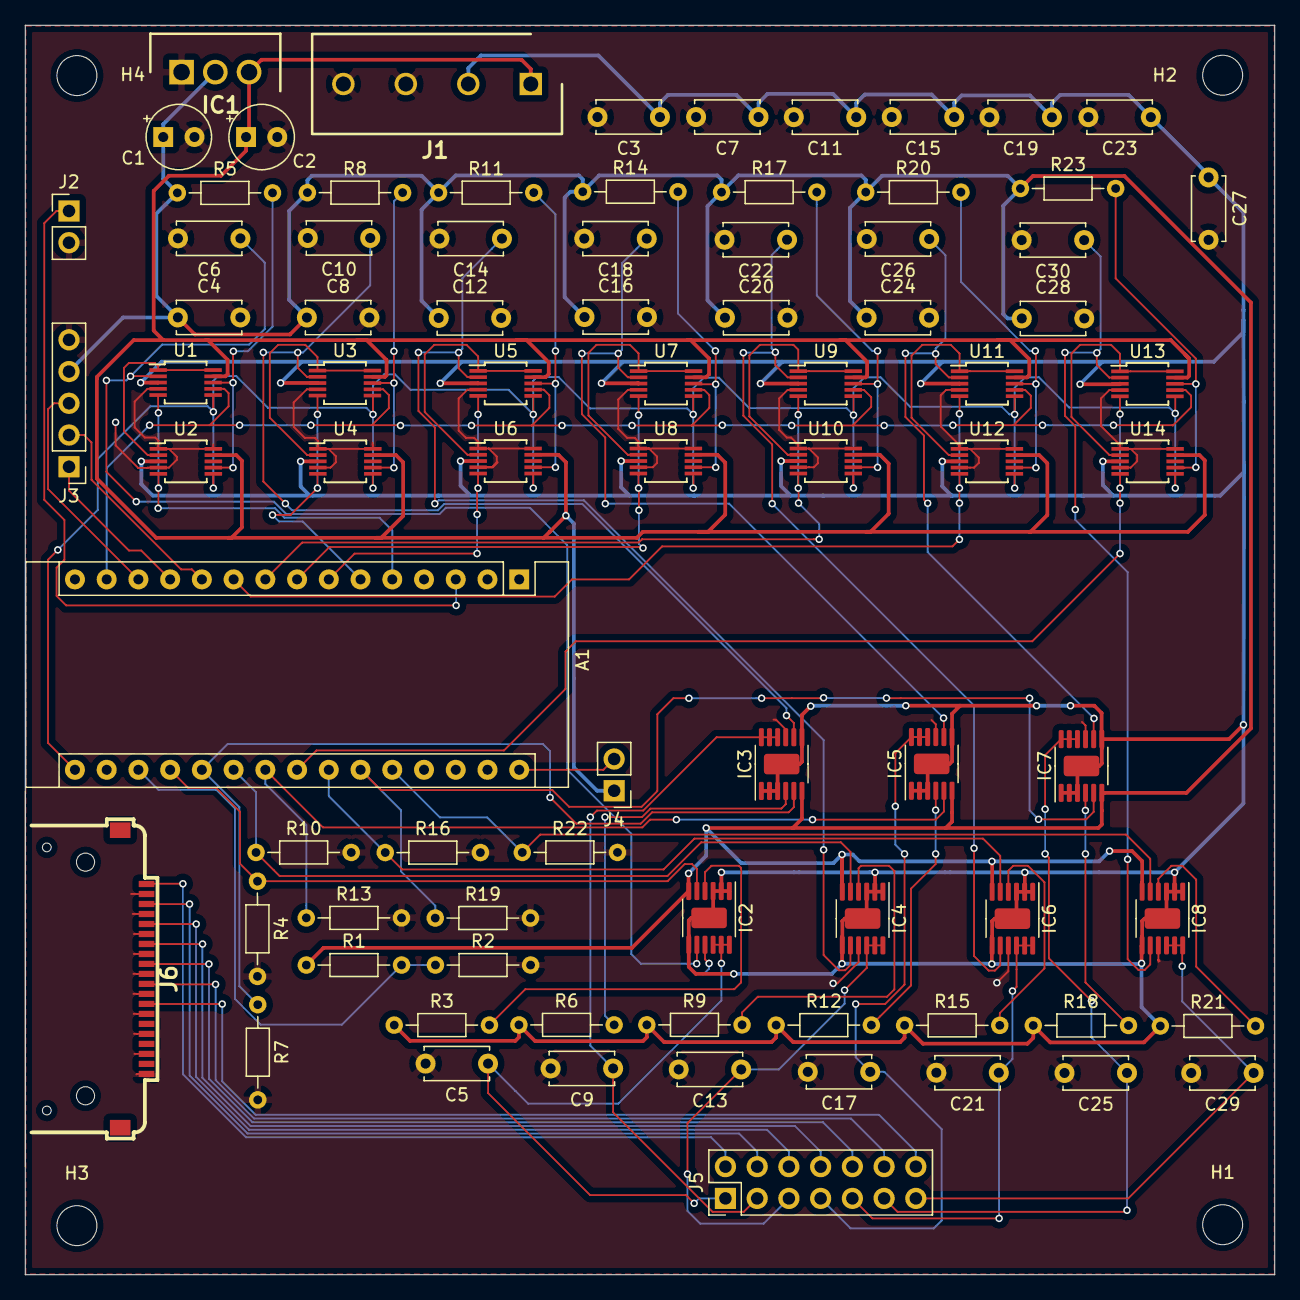
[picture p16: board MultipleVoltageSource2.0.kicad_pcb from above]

Board: 2 copper layers, 100.0 x 100.0 mm, 86 parts (0 on the bottom side), 68 nets.

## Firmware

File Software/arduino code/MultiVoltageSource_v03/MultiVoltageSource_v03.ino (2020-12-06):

// ******************************************************
// Multiple Voltage Source v0.3
// 31 de Julio 2020
// Author: Antonio Perez-Serrano, CEMDATIC-ETSIT (UPM)
// ******************************************************

// include libraries
#include <SPI.h>
#include "Wire.h"
#include "Adafruit_LiquidCrystal.h"

// LCD Connected via SPI
Adafruit_LiquidCrystal lcd(8, 10, 9);

// Chip Select Pins for the Different Channels
const int ChipSelect_Ch1 = 2;
const int ChipSelect_Ch2 = 3;
const int ChipSelect_Ch3 = 4;
const int ChipSelect_Ch4 = 5;
const int ChipSelect_Ch5 = 6;
const int ChipSelect_Ch6 = 7;
const int ChipSelect_Ch7 = A4;

// Current Measurement Pins for the Different Channels
const int CurrMes_Ch1 = A0;
const int CurrMes_Ch2 = A1;
const int CurrMes_Ch3 = A2;
const int CurrMes_Ch4 = A3;
const int CurrMes_Ch5 = A5;
const int CurrMes_Ch6 = A6;
const int CurrMes_Ch7 = A7;

// Other variables
String received;
int channel = 1;
int received_value;
long aux_int = 0;
int vec_valuesR[] = {0,0,0,0,0,0,0};
int vec_valuesI[] = {0,0,0,0,0,0,0};

// include our functions file
#include "functions.h"

// *********************************************
// SETUP
// *********************************************
void setup() {

  // set up the LCD's number of rows and columns: 
  lcd.begin(20, 4);
  // Print a message to the LCD.
  lcd.setCursor(4, 0);
  lcd.print("CEMDATIC-UPM");
  lcd.setCursor(0, 1);
  lcd.print("MultiVoltSource v0.3");
  lcd.setCursor(6, 2);
  lcd.print("Welcome!");
  lcd.setCursor(0, 3);
  lcd.print("starting...");
  
  // Chip Select Pins initialize:
  pinMode(ChipSelect_Ch1, OUTPUT);
  pinMode(ChipSelect_Ch2, OUTPUT);
  pinMode(ChipSelect_Ch3, OUTPUT);
  pinMode(ChipSelect_Ch4, OUTPUT);
  pinMode(ChipSelect_Ch5, OUTPUT);
  pinMode(ChipSelect_Ch6, OUTPUT);
  pinMode(ChipSelect_Ch7, OUTPUT);
  // Setting all Chip Select Pins to HIGH
  digitalWrite(ChipSelect_Ch1, HIGH);
  digitalWrite(ChipSelect_Ch2, HIGH);
  digitalWrite(ChipSelect_Ch3, HIGH);
  digitalWrite(ChipSelect_Ch4, HIGH);
  digitalWrite(ChipSelect_Ch5, HIGH);
  digitalWrite(ChipSelect_Ch6, HIGH);
  digitalWrite(ChipSelect_Ch7, HIGH);
  
  // Serial begin
  Serial.begin(1000000);
  // initialize SPI
  SPI.begin();

  for (channel=1; channel<8; channel++){ 
    digitalPotWrite(channel, vec_valuesR[channel-1]);
  }
  delay(2000);

  // First current reading
  readCurrent();
  
  // Ready message
  lcd.clear();
  lcd.setCursor(0, 1);
  lcd.print("Ready!");
  lcd.setCursor(0, 2);
  lcd.print("waiting serial...");
  
  delay(2000);
  
}

// *********************************************
// LOOP
// *********************************************
void loop() {

    Serial.flush();

    aux_int++;
    
    while ( Serial.available() > 0 ){
      received =  Serial.readStringUntil('$');

      Serial.println(received.length());
      
      channel = received.substring(0,1).toInt();
      vec_valuesR[channel-1] = received.substring(2,received.length()).toInt();
      
      Serial.println(channel);
      Serial.println(received);
      
      if (received_value >= 0 & received_value < 511){
        digitalPotWrite(channel, vec_valuesR[channel-1]); 
        displayLCD(vec_valuesR, vec_valuesI);
      } else {
        Serial.println("No valid");
      }
                
    }

    if ( aux_int == 200000 ){
      readCurrent(); 
      aux_int = 0;
      displayLCD(vec_valuesR, vec_valuesI);
    }
    

}
